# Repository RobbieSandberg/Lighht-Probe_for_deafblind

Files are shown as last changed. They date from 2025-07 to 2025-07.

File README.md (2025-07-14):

  # Light Probe with Vibration for Blind and Deafblind People
## Project Description
The light probe indicates light sources by vibration. The more light hits the probe, the stronger the vibration.  
This allows users to check whether a light is on in a room, where the windows are located, whether the sun is shining, etc.  
For example, if you turn toward a light source with the probe in your hand, the vibration increases. By sweeping the probe side to side, the direction of a light source can be easily detected.

## Features
- Measures light intensity using a photoresistor (LDR)  
- Converts light intensity into vibration strength  
- Uses a coreless vibration motor  
- Controlled by a microcontroller (Arduino Nano Every)  
- Compact design by 3D-printed enclosure  
- Ideal for blind and deafblind users  

## Project Contents
- **Firmware:** Microcontroller code for Arduino  
- **Hardware:** Circuit diagram, pinouts, and wiring guide  
- **Enclosure:** 3D files (STL)  
- **Documentation:** User guide, assembly instructions, bill of materials, and building notes  

## Bill of Materials
The following components are linked to product pages. For the vibration motor, push button, and battery holder, the exact linked products are required, as the enclosure is designed to fit them.  
This does not apply to generic parts like the Nano, breadboard, or LDR.  
Estimated total cost (subject to price changes): €24.50

- 1 [Arduino Nano]( https://www.amazon.de/gp/product/B07WWK29XF)  
- 1 [Mini Breadboard]( https://www.amazon.de/Elegoo-Points-Mini-Breadboard-Arduino/dp/B01M9CHKO4) (170 tie points) or 1 [expansion board]( https://funduinoshop.com/bauelemente/verbinder/klemmen/nano-r3-expansion-board-fuer-schraubklemmen) with screw terminals  
- 1 [Photoresistor]( https://www.amazon.de/dp/B082X5JY71) (LDR) – crimping required  
- 1 [Vikye Coreless Vibration Motor]( https://www.amazon.de/gp/product/B07TS7WR67) – crimping required  
- 1 [Gebildet 12mm Stainless Steel Push Button]( https://www.amazon.de/dp/B09Q8F5JR3) – crimping required  
- 1 [SDENSHI 9V Battery Holder]( https://www.amazon.de/gp/product/B082RKZTFW) – crimping required  
- 5 [Jumper Wires]( https://www.amazon.de/VoltMate-kompatibel-Arduino-Raspberry-Breadboard/dp/B0CX5MGPWT) (male-to-female)  
- 1 Resistor 10 kΩ  

**Required tools:** needle-nose and/or flat pliers, Phillips screwdriver, optionally ducked or double-sided tape

## The Circuit
The circuit can be built using an Arduino Nano and a mini breadboard or a screw terminal shield – both fit into the enclosure.  
Sighted people may of course solder.

- One pin of the LDR goes to 5V, the other to the 10 kΩ resistor and to A0 (voltage divider)  
- The other pin of the resistor goes to GND  
- The vibration motor connects to D11 and GND  
- The battery connects with its positive terminal via the push button to VIN and with its negative terminal to GND  

With the specified battery holder: the wires come out corresponding to the polarity of the inserted battery.  
If the wires point away from the body and the clip is on the left, the right wire is positive and the left one is negative.

## Enclosure Description
“Front” and “rear” refer to positions relative to the enclosure. How the device is oriented or held during assembly is up to the builder.

The enclosure body is a tube open at both ends, tapering slightly toward the front.  
At the rear end, there are four notches around the edge and four cylinders on the inner wall.  
These notches align with the corners of the battery holder. This allows for the smallest possible outer dimensions, as the front of the battery holder is not fully enclosed.  
When the holder is inserted with its corners in the notches, the holes in the front panel align with screw mounts in the cylinders.

Inside, roughly in the middle, there is a platform to support the breadboard with its wiring.  
Beneath this platform, so between it and the enclosure wall, is the socket for the vibration motor.  
Just before the front end, there is a hole for the push button.  
On the front rim, an internal screw thread is located.

The enclosure tip is cone-shaped. Its base has a thread, and its tip has a hole for the LDR.  
Inside, just before the hole, is a ring that acts as a lock for the expansion plug.

The expansion plug is a blunt cone with two lateral grooves and one groove on the bottom.  
At the bottom, there are two vertical tabs parallel to the center groove.

## Assembly
If using a breadboard, it is recommended to secure the circuit with tape to prevent components from coming loose during insertion.  
If using a screw terminal shield, tape is not required, but double-sided tape must be applied to hold the shield in place.

The entire circuit can be pre-wired before installation.  
Only the push button must be disconnected before inserting.

First, feed the LDR (attached to long jumper wires) through the rear and pull it out the front.  
Do the same for the wires of the vibration motor and the push button.  
The vibration motor is inserted into its socket from the front.  
Peel the protective backing from the breadboard and gently insert it.  
Make sure the board is placed on the platform so that nothing sticks out at the back, as the platform aligns with the battery holder.

Now the battery holder should be inserted and screwed down, so that the rest of the assembly is easier.  
Make sure no wires are jammed between the battery holder and the breadboard.

Insert the push button from the outside into the hole. From the inside, fasten the nut onto the button and tighten it.  
Reconnect the wires to the button.

Next, place the LDR’s pins into the side grooves of the expansion plug so the sensor lies on top of the plug.  
Now insert the plug into the cone tip using pliers.  
Squeeze the bottom tabs together until the base of the plug passes the inner ring. This ring locks the plug in place at the tip.

Finally, screw the cone tip onto the body and tighten firmly.

## License
© 2025 Robbie Sandberg  
This project is licensed under the Creative Commons Attribution – NonCommercial 4.0 International License (CC BY-NC 4.0).

You are allowed to:  
- Build the device  
- Use, share, and modify the designs  
- Use the work in non-commercial contexts (school, personal, self-help)

You are not allowed to:  
- Sell the designs or derived devices  
- Use them commercially (advertising, paid workshops, etc.)  
- Share the work without attribution

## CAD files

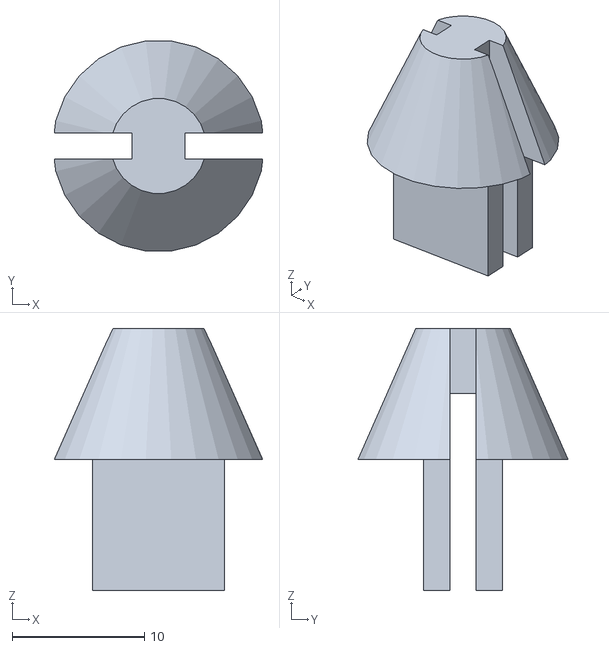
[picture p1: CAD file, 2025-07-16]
NosePlug.stl
15.8 x 15.9 x 19.8

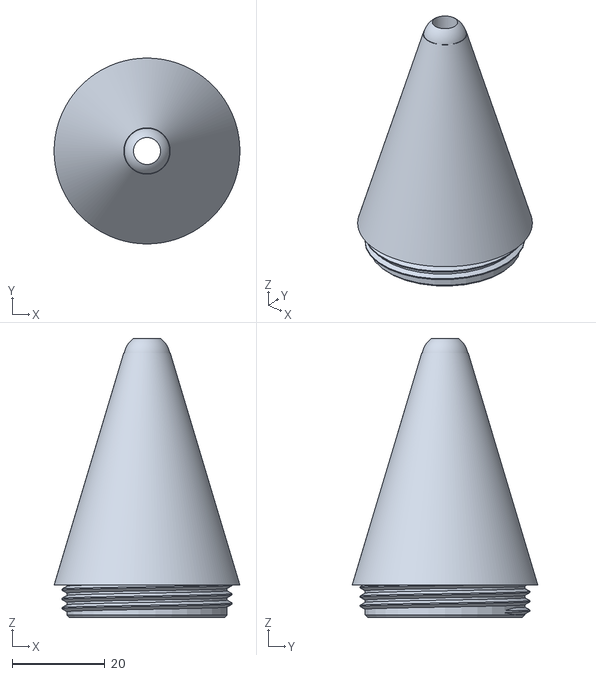
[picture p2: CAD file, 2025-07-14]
NoseCone.stl
40.0 x 40.0 x 60.1

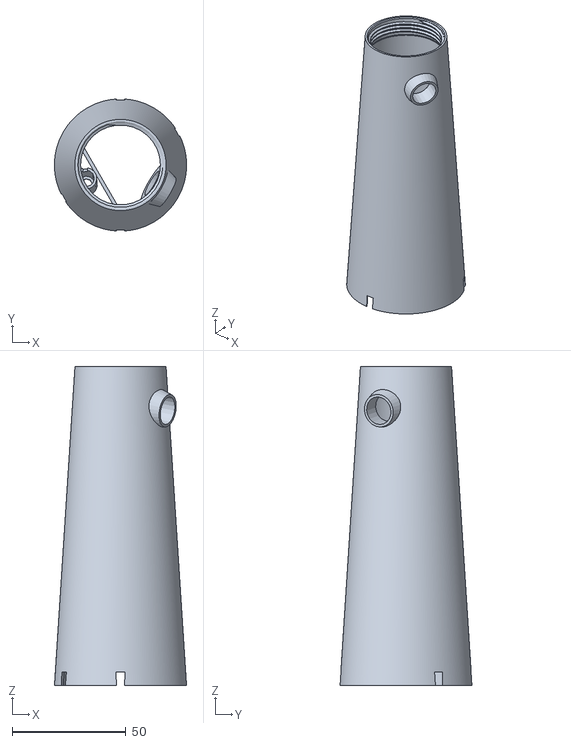
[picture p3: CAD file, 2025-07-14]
Fuselage.stl
58.0 x 57.9 x 140.0

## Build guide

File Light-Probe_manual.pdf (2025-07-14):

## Light Probe – User Manual

The probe has a round body shaped like a rocket. At its tip, the probe has a

small hole. This is where the light is measured.

Just below the rocket nose, there is a button. You can comfortably hold the

probe in your hand and press the button with your thumb.

The button must be held down during use.

When the button is pressed and held, a short vibration pulse occurs. This

indicates that the probe is ready for operation and that light sensoring has

begun.

If no vibration pulse occurs after pressing the button, the battery must be

replaced.

If you do not feel a vibration after the first pulse, the probe does not register

any light.

This does not necessarily mean that it is completely dark. The probe can only

measure light it encounters directly. For example, if your body is between the

probe and a light source, the probe will not vibrate.

You can turn through 360° or pan the probe to locate possible light sources.

Since the measurement takes place at the tip of the probe, the direction of a

light source can be easily determined. The direction the tip points to is where

the light comes from.

### Battery Replacement

The battery compartment is located at the bottom of the probe. It is

rectangular.

The latch is on one of the short sides of the rectangle. It is a spring clamp

that can be pressed toward the other short side of the rectangle with a

fingernail.

The probe should be held so that the spring clamp is on the left side.

It can then be easily opened with the thumbnail of the right hand.

If done correctly, the battery drawer will release, and you can pull it out with

your thumb and forefinger. The drawer can be completely removed from the

battery compartment.

The battery can be pushed out from the bottom of the drawer.

When inserting a battery, the drawer should be held so that the cutouts for

the battery connectors point away from your body.

The battery terminals should also point away from your body.

In this position, the large terminal belongs on the left and the small terminal

on the right.

The battery cannot be inserted incorrectly because the drawer has precisely

fitting cutouts for the terminals.

The battery should be lowered into the drawer from above.

The drawer is then slid back in with the spring clamp on the left until the

clamp snaps into place.

Maintenance

The enclosure consists of two components: the body and the nose.

The body and nose are screwed together. If the nose loosens after prolonged

use, it can be firmly tightened clockwise.

Opening the device by unscrewing it may damage the electronics.

The enclosure is made of PLA and should not be left in direct sunlight for

extended periods. Using it in sunshine is safe.

© 2025 Robbie Sandberg – This manual is licensed under CC BY-NC 4.0

Project page on GitHub:

https://github.com/RobbieSandberg/Lighht-Probe_for_deafblind

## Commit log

2025-07-14 Initial project upload
    [Fuselage.stl, NoseCone.stl, NosePlug.stl]
2025-07-16 Updated for better grip
    [NosePlug.stl]
